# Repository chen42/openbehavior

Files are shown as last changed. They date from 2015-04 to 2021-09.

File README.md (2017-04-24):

# OpenBehavior

This project aims to establish a computing platform for rodent behavior research using the Raspberry Pi computer. We are building devices for conducting operant conditioning, as well as some infrared sensor based assays. We also designed an environmental sensor set that records the temperature, humidity, air pressure, ambient light, noise level, etc. 

These projects are in various stages of development. The following are the most mature projects.

## Operant Licking
This project develops a home cage device for operant licking (fixed ratio, various ratio, or progressive ratio schedules). Detailed description of this project is published in a [PeerJ article]( https://peerj.com/articles/2981/) 

## EnvSensors

This device collects four environmental variables and we have several of them running in the lab. This device is also described in our [PeerJ article](https://peerj.com/articles/2981/)

## RFID 

This project develops a standalone RFID reader for the EM4100 implantable glass chips. We use this daily in the lab.

## Extinction

This device is used to run extinction experiments as described  by [Wang et al. (2014)](www.ncbi.nlm.nih.gov/PubMed/25532105) 

## Motion

This project adds a motion sensor to standard operant chambers.

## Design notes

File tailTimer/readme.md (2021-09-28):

# TailTimer: Automating the tail immersion assay 

# Please do not pull from this repo. Tailtimer submodule has been moved to [this](https://github.com/chen42/tailTimer) repo. All updates will be done there.

The tail immersion assay is a widely used method for measuring acute thermal pain in rodents. TailTimer  uses the Raspberry Pi computer to automatically record both tail withdrawal latency and water temperature. The device has a radio frequency identification (RFID) system that can record the ID of animals. The software recognizes several specific RFID keys as user interface commands, which allows TailTimer to be operated via RFID fobs. We also programmed the device to only allow tests to be conducted when the water is within ± 0.25 °C of the target temperature.

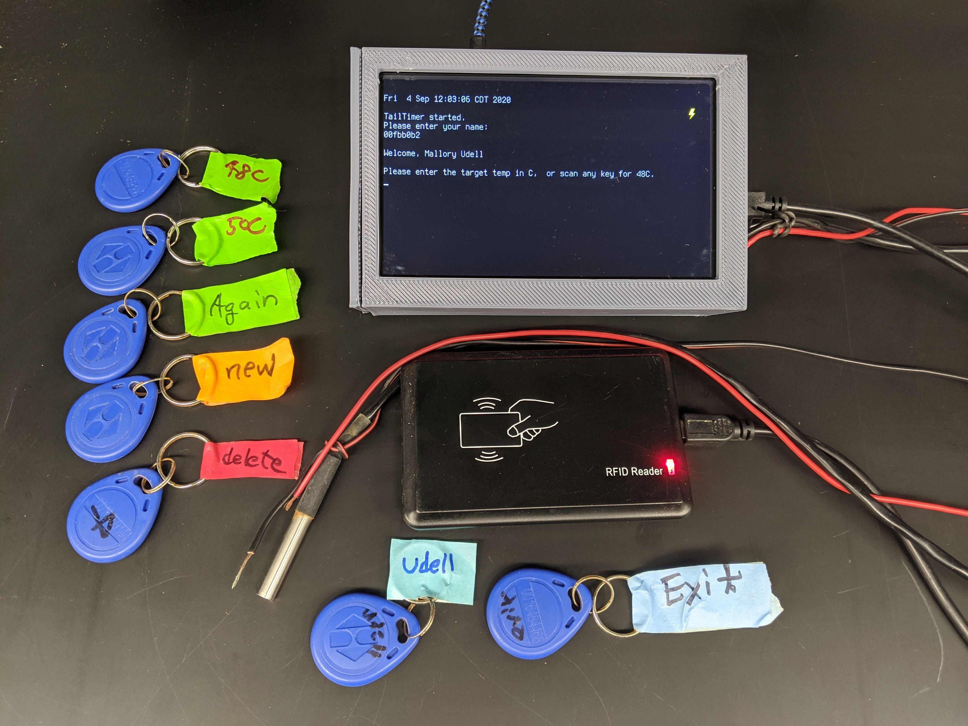
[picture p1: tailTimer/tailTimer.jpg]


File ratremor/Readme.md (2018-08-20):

#Ratremor

Tremor is a common sign of withdrawal from abused drugs. By fixing an ADXL345 accelerometer to the bottom of a platform that is sitting on a set of four balanced springs, we are testing if the z-axis data can be used to measure tremor in rats.

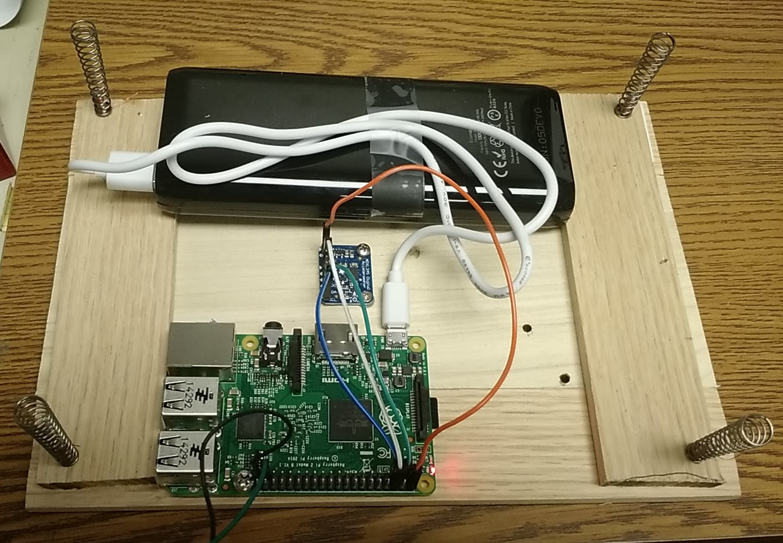
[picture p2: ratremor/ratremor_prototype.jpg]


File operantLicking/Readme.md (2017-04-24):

# Operant Licking

This device uses a RPi to record the licking events on two spouts. It then drives a syring pump to deliver a fixed amount of liquid to the spout, based on the reinforcement schedule in effect (fixed, variable, or progressive ratio).  

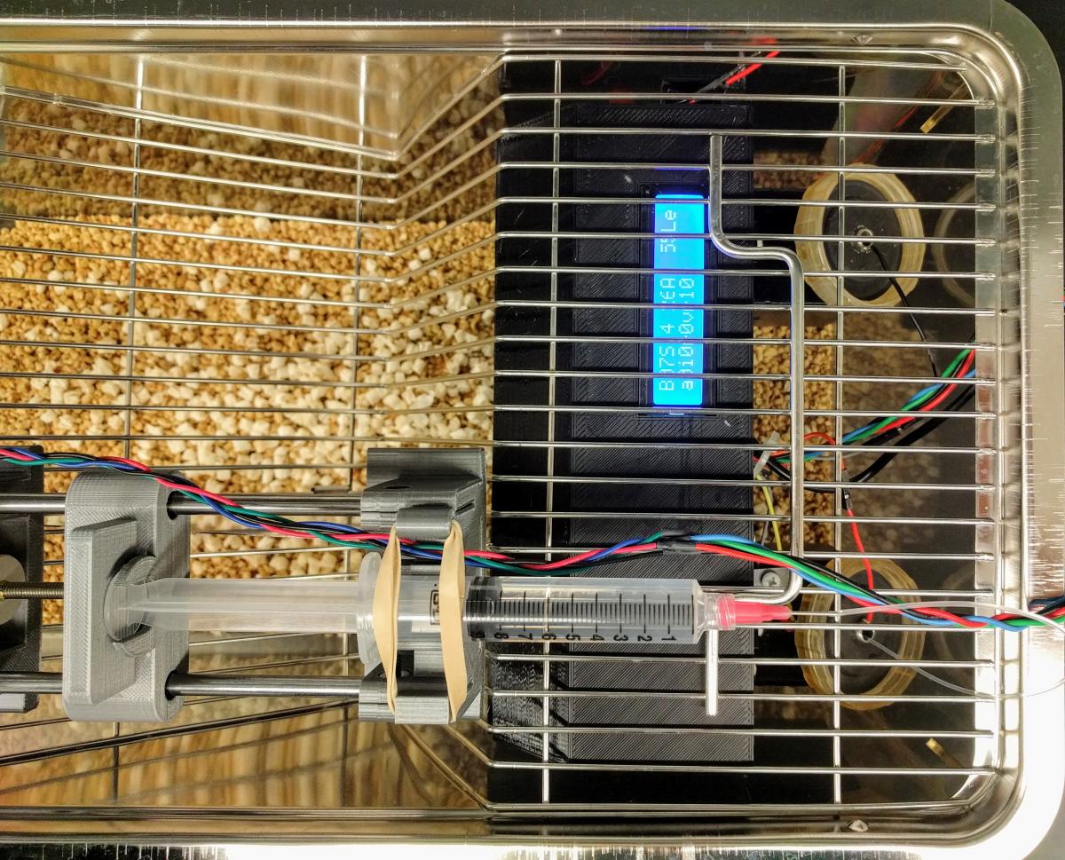
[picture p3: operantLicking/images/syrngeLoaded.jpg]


## [Parts list](PartsList.md) 

## [Assembly instruction](Assembly.md)

Detailed description is published in this [PeerJ Article](https://peerj.com/articles/2981/)

A video of rat licking for sucrose under a VR10 schedule is available [here](https://youtu.be/l3SEo6oAtPM)

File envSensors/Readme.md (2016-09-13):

# Using the Raspberry Pi single board computer to monitor the lab environment

The sensor we use include the HTU21DF for humidity,  TSL2561 for light,  and BMP180 for barometric pressure. Both the HTU21DF and BMP180 have a temperature sensor. So we take the average readout of the two. These sensors are all connected to the Raspberry Pi via I2C.  We also use a I2C  real-time clock (DS1307 from either Adafruit or JBtek. JBtek is cheaper but some of the units we got were not reliable) to ensure the accuracy of the time.  

The location of the device is identified in a file named deviceid located at /home/pi/. The ID stored in this file is used to name the data file. This ID is also entered in the data file. This allows the same program to be deployed at multiple locations. The python logger program is run once every 10 min via cron.

We use this device to monitor the environment of animal housing rooms where the light cycle is reversed. The logger program  writes the lux level during the night to a file called lux.csv. The checklux.py program, also ran via a cron job, checks the lux level during the day and flashes an LED to alert the technician if lights are off during the night.    

## Parts list

Raspberry Pi 2B or 3  [Element 14] (https://www.element14.com/community/community/raspberry-pi)

TSL2561 Lux Sensor [Adafruit] (https://www.adafruit.com/products/439)

BMP180 Pressure Sensor [Adafruit] (https://www.adafruit.com/products/1603)

HTU21D-F Humidity Sensor [Adafruit] (https://www.adafruit.com/products/1899)

SB4 Snappable PC BreadBoard [Amazon] (https://www.amazon.com/gp/product/B00PX52C7Q)

1P-1P female to Female Jump Wire [Amazon] (https://www.amazon.com/gp/product/B00R96X8JS)

Edimax USB WiFi module, not needed if use RPi 3B [Amazon] (https://www.amazon.com/Edimax-EW-7811Un-150Mbps-Raspberry-Supports/dp/B003MTTJOY/)

## Assembly 

### Add wires to the sensors

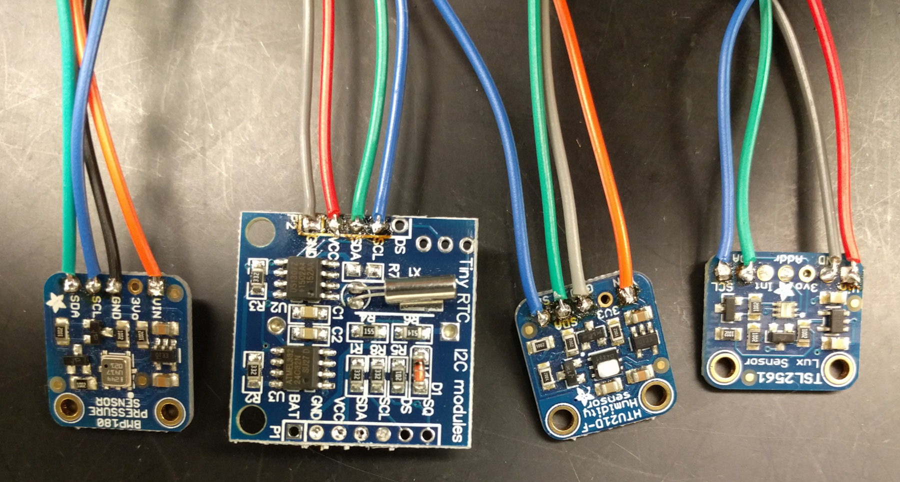
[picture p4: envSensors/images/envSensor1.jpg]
Cut the jumper wire in half. Solder four wires to each sensor (and RTC). We use black (or grey) for ground, red (or orange) for 5V, blue for SCL, and green for SDA. 

### Prepare the breadboard
Drill four holes at the corners. Solder four rows of pin heads (five pins each) to the snappable breadboard. 
We use the two side rows for the GND and 5V. Use the middle two rows for SDA and SCL. 
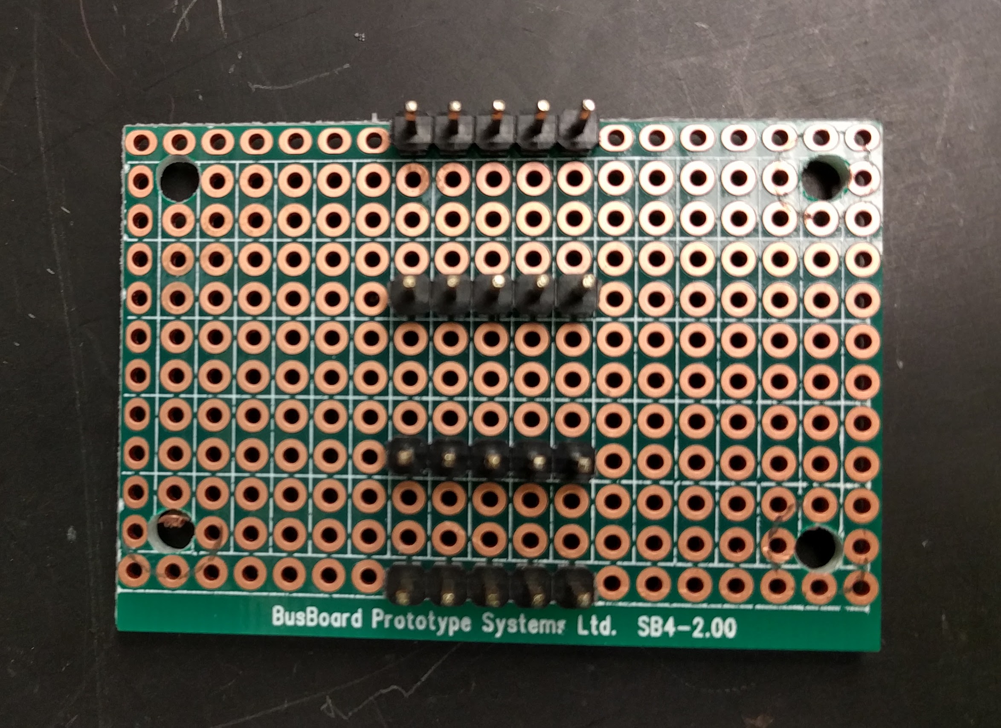
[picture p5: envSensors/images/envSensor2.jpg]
.

Make sure pins on the same head are all connected at the back. (You can solder a short segment of wire to two middle pin heads to connect them).  
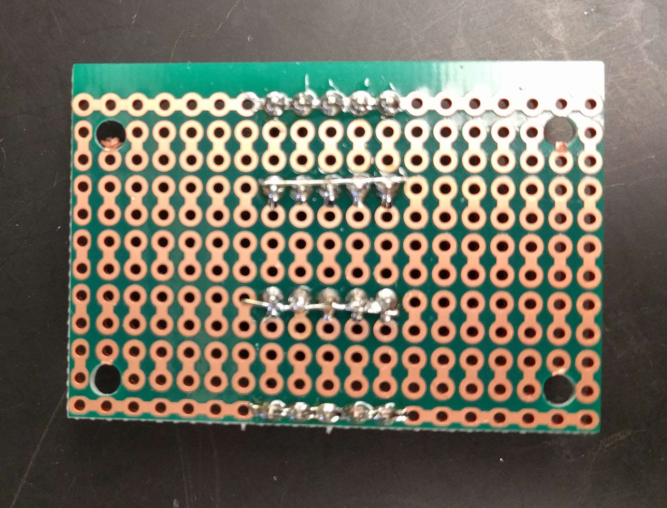
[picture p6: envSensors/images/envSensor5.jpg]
.

### Connect the wires

Connect the sensors and the real-time clock to the pins.
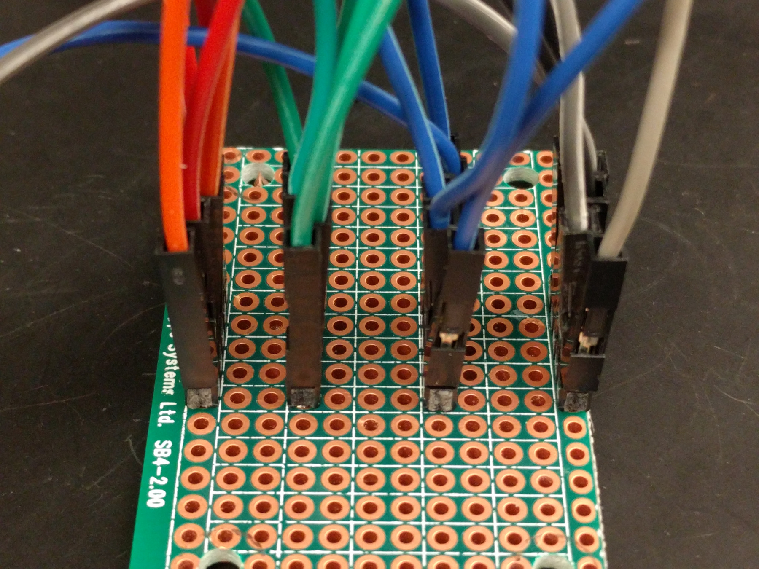
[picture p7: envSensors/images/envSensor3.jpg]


Use one additional sets of four wires to connect the last set of pins to the GND, 5V, SCL, and SDA pins on the RPi.

### Final step

Screw the parts to the 3D printed base.
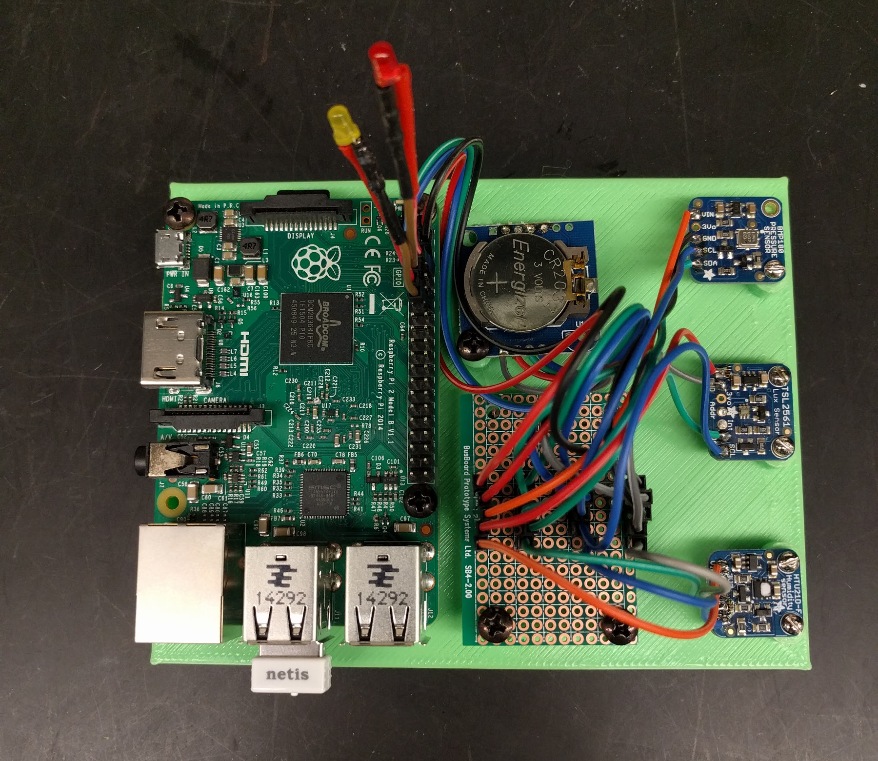
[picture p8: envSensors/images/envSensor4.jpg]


## Software

Clone the repository
```
cd /home/pi/
git clone https://github.com/chen42/openbehavior.git
```

Enable the realtime clock by following these [instructions](https://learn.adafruit.com/adding-a-real-time-clock-to-raspberry-pi/overview)

Edit the /etc/rc.local file to include the following lines  (needed by the RTC and HTU21D-F sensor library)

```
echo ds1307 0x68 > /sys/class/i2c-adapter/i2c-1/new_device
pigpiod &
```

Run the following command to edit cron 

```
sudo crontab -e
```

Add the following line will run the EnvSensor script once every 20 min.

``` 
*/20 * * * python /home/pi/openbehavior/envSensors/env_logger.cron.py 
```

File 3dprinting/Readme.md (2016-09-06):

Design files for 3D printing 
==============================

The frames or cases used for the various devices are located in the devices folder. Here are some misc. objects that we use in the lab. Older files were designed using using <a href="http://freecadweb.org/">FreeCAD</a>. Newer files were designed uing <a href="http://www.openscad.org">Openscad</a>.  You can click on the .stl file and view a 3D rendering of the design using Github's built-in viewer.

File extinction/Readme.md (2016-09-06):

# Using a Raspberry Pi to run extinction sessions

We have several old operant chamber where the electronics are starting to fail. This project uses a RPi to record the number of licks on two spouts. There is also a constantly flashing visual cue during the session. We now use these to run the contextual extinction sessions as described in our earlier papers <a href=https://www.ncbi.nlm.nih.gov/PubMed/25532105> by Wang et al. (2014)  </a> and  <a href="https://www.ncbi.nlm.nih.gov/PubMed/25566005"> by Wang et al. (2014) </a>. ￼ 

The *extinctionCase* holds the RPi.  The *extinctionCueLightPlate* holds the cue light for one side. The *extinctionCueLightBox* is inserted into the *extinctionCase* and holds the other set of cue lights. The *extinctionCaseCover* has an opening for an LCD, which displays session info and data. 

The device is running either from a 5V DC microusb power supply or using a large 5V cell phone backup battery.

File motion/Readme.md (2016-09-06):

#Adding  motion sensors to operant conditioning chambers

## Description
This project adds a motion sensor to the commercial MedPC operant chambers. The motion sensor is controlled by a RPi. The RPi is powered by the 28V power source available in the operant chamber (via a step down converter). The RPi is turned on and off via MedPC programs. The data are stored in the SD card of the Pi. Each operant chamber use one Pi. All the Pi computers are connected by a WiFi network and data are transferred to a remote server via sftp.

## Parts list

Molex connector for 28V. Mfg P/N: 03-06-2032 [Mouser] ( http://www.mouser.com/ProductDetail/Molex/03-06-2032/?qs=%2fha2pyFadugvI%2fznVBilJA6N4bQxmqBpdBoCzb%2f9bbY%3d)  

Molex pin. Mfg P/N: 02-06-2103 [Mouser] (http://www.mouser.com/ProductDetail/Molex/02-06-2103/?qs=%2fha2pyFaduhC0HER4S2%2flGJ0%2fQN3qzJ5F27g%252bKWL4TY%3d)

Motion sensor. [Amazon] (http://www.amazon.com/gp/product/B00FDPO9B8) 

EdiMax WiFi USB. [Amazon] (http://www.amazon.com/gp/product/B003MTTJOY)

Step-down LM2596 power converter. [eBay] (http://www.ebay.com/itm/161476280982)  

## Notes

Two step down DC-DC converters are used. One is set to 5 V to power the RPi. This is always on. The other one is set to 3.3 V. This is only on when the output port in the MedPC is activated. This then controls the on and off of the motion.py program.

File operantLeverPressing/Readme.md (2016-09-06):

#Operant Lever Pressing 

This is one of the earliest attempts we had. It uses a RPi to monitor two levers (i.e. switches). The output is a dry food pellet deliverying device.

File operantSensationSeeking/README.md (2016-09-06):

# Operant Senstation Seeking

This is a device for operant sensation seeking. This needs improvements in several areas based on the alcohol self-admin device. It will be updated when I have time.

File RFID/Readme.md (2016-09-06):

# Standalone RFID Reader

This is a simple device that connects an RDM 6300 RFID reader board to the RPi. The ID of the glass tags is  shown on the LCD.

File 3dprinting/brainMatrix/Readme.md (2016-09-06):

# Brain slicer

## Assembly
See brainMatrix_assembled.stl.  The other three stl files are for printing.

## Procedure
A fresh rat brain is placed in the cutter. Single edge blades are then lowered into the guide slots of the cutter to cut the brain at 1 mm intervals. The slider is then moved out, allowing the cutter to be lowered into the base. The side bars of the base catch the blades and allow the brain sections to be removed one at a time.

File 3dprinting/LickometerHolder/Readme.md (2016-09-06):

# Water spout holder for operant chambers

The tilted bottom one prevents extra liquid causing short circuits. The tall one allows rats with head stages to access the spout. These fits in the standard operant chambers for rats.

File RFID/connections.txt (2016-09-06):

RDM 6300 connections
-------------------
The antenna can be connected in either direction
connect the Tx on the RPi (i.e. pin 8)  to Rx on the board (i.e. PIN 2) 
connect the Rx on the RPi (i.e. pin 10) to Tx on the board (i.e. PIN 1)  
connect the ground on the RPi (i.e. pin 6) to the ground on the board (i.e. Pin 4)
connect the 5V on the RPi (i.e. pin 2) to the power in on the board (i.e. Pin 5)

LCD connections
--------------
RS -> Pin 03 / GPIO 02
EN -> Pin 05 / GPIO 03
D7 -> Pin 07 / GPIO 04
D6 -> Pin 11 / GPIO 17
D5 -> Pin 13 / GPIO 27
D4 -> Pin 15 / GPIO 22

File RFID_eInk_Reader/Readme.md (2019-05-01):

# This is a RFID reader with an eInk hat display

## 2.7 inch e-paper hat
* From [WaveShare.com](https://www.waveshare.com/2.7inch-e-Paper-HAT.htm)
* User manual in [PDF](https://www.waveshare.com/w/upload/3/31/2.7inch_e-paper_hat_user_manual_en.pdf)

## RFID USB reader 
* https://www.amazon.com/Reader-LANMU-125khz-Contactless-Proximity/dp/B07B7H6CQ2

## Software
* Library https://github.com/waveshare/e-Paper/tree/master/2.7inch_e-paper_code/RaspberryPi/
* Steps not described in the user manual
	* enable SPI interface in the PI ```sudo raspi-config```
* For the python demo code from waveshare, make sure the font is present in your system. 
* To run the python code automatically after boot, do the following
  * change the boot into command line and enable auto login with user pi by running ```sudo raspi-config```  
  * add the python program to the end of the .bashrc file for user pi

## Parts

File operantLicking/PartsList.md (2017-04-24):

# Parts list  

Qty 1 for most parts, unless otherwise stated.

Most parts can be purchased from Amazon or Ebay by searching the model number.  

## Operant Licking Device 

Raspberry Pi Model 2B or newer [Element 14](https://www.element14.com/community/community/raspberry-pi).

Edimax WiFi USB connector Model:  EW-7811Un N150 USB 2.0 (not needed for Raspberry Pi 3 or newer).

DS1307 realtime clock with dual I2C connections (Model: AT24C32 IIC) 

12V AC-DC converter (2 Amp) [Amazon](https://www.amazon.com/gp/product/B00PJZQDDO/).

DC-DC step down module adjustable to 5V (Model: LM2596s ASIN: B00W94HW8S) 

Touch sensor (Model: MPR121, 12 channel) [Adafruit](https://www.adafruit.com/products/1982).

Motion sensor (Model: HC-SR501)  

RFID reader (Model: RDM 6300) [Amazon](https://www.amazon.com/gp/product/B00KBN01VY/).

RFID glass tags and injection syringe (EM4100 encoding) [AliExpress](https://www.aliexpress.com/item/RFID-glass-4x20-application-logistics-patrol-asset-identification-management-security-frequency-125KHZ/931328784.html).

LCD 16 x 2 characters (Model HD44780)  

10K ohm potentiometer (if the LCD does not come with one) [Amazon](https://www.amazon.com/gp/product/B00OK9DEL4).

5 mm LED (white, for cue light).

3 mm LED (Assorted colors, for signals).

100 om resister Qty: 3.

Omal (TM) 2 x 40 pcs 20 cm 1P-1P female to female bread jump wire (or other brands).

Stainless steel flux, such as  [Amazon](https://www.amazon.com/gp/product/B001HWE9A2) 

Solid core Hook-up Wire 22 AWG  [Sparkfun](https://www.sparkfun.com/products/11367)

### Syringe Pump

LM6UU linear ball bearing bushing  Qty: 2 per pump [Amazon](https://www.amazon.com/gp/product/B00NQ2DPV0).

625Z single shielded deep groove ball bearing  [Amazon](https://www.amazon.com/gp/product/B008ASXTZM/).

NEMA 11 step motor [Pololu](https://www.pololu.com/product/1205). 

Elegoo Step motor controller with heat sink (Model: A4988) [Amazon](https://www.amazon.com/gp/product/B01GJJGRF2).

18-8 Stainless stell threaded Rod M5-0.8 thread [Amazon](https://www.amazon.com/gp/product/B00G3R7J1W/).

CND motor shaft coupler 5mm to 5mm [Amazon](https://www.amazon.com/gp/product/B00DCAISM2).

Steel Rod 6mm Diameter [Amazon](https://www.amazon.com/gp/product/B0050RMVLE).

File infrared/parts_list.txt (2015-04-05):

items from sparkfun.

Infrared Emitter & Detector Set:
SEN-00241

Emitter:
LTE-302

Detector:
LTR-301

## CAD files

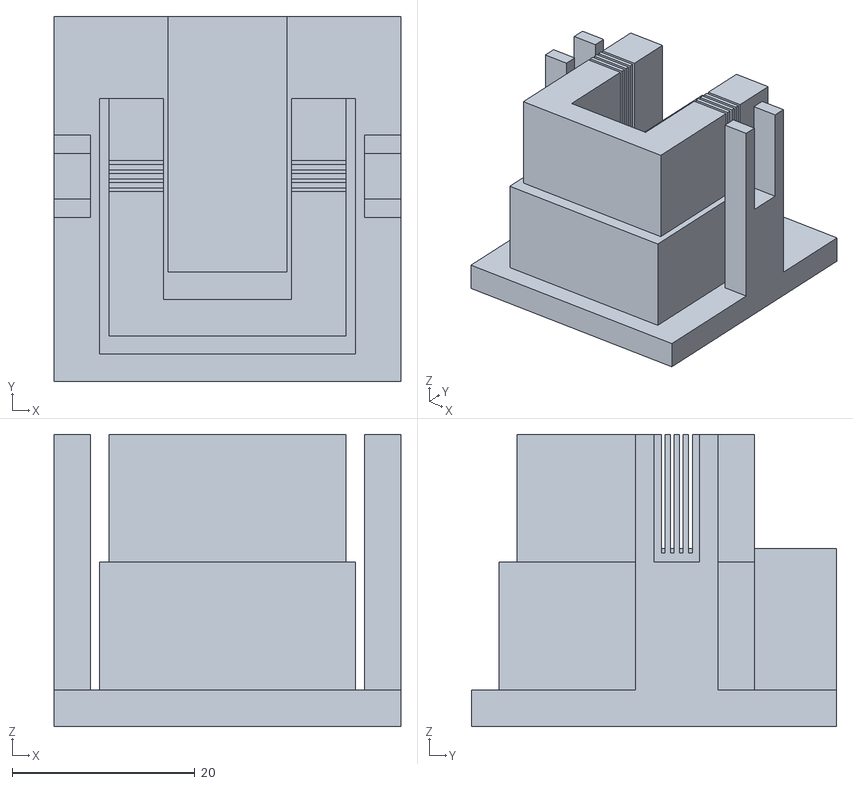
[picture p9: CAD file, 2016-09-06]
3dprinting/brainMatrix/brainMatrix_assembled.stl
38.0 x 40.0 x 32.0

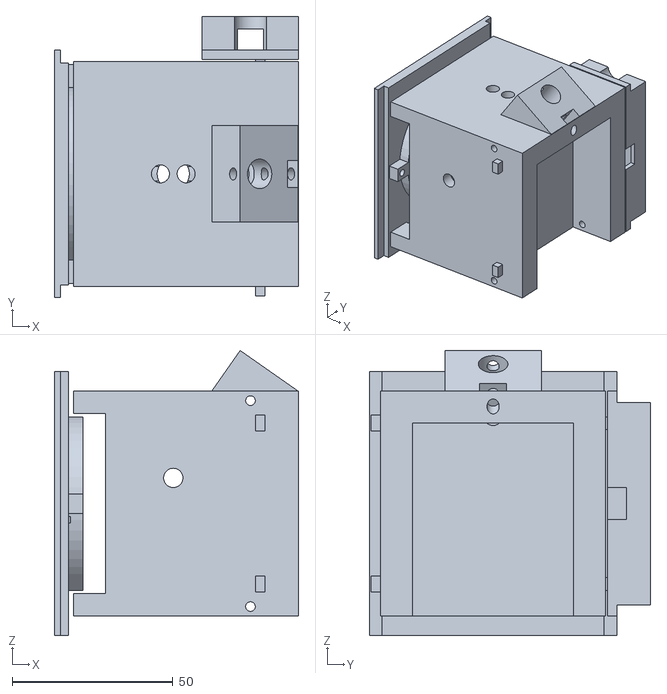
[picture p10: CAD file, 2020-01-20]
socialDrinking/openscad/rfid_waterspout_complete.stl
76.0 x 87.5 x 88.6

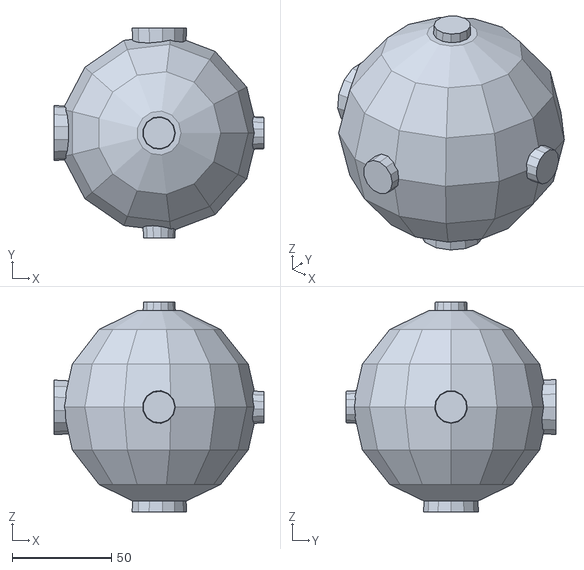
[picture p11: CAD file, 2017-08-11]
3dprinting/ball/ball_lo_res.stl
106.0 x 106.0 x 106.0

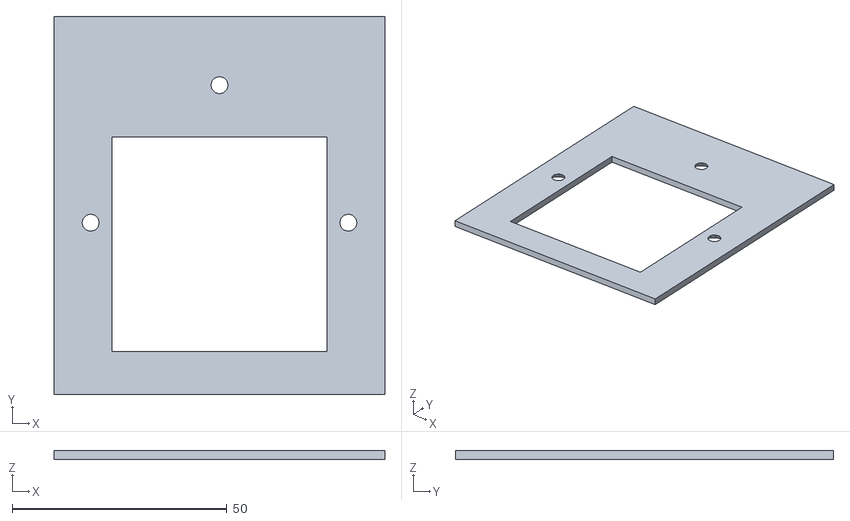
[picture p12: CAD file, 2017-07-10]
3dprinting/LickometerHolder/operant_chamber_spout_holder_plate.stl
77.0 x 88.0 x 2.00

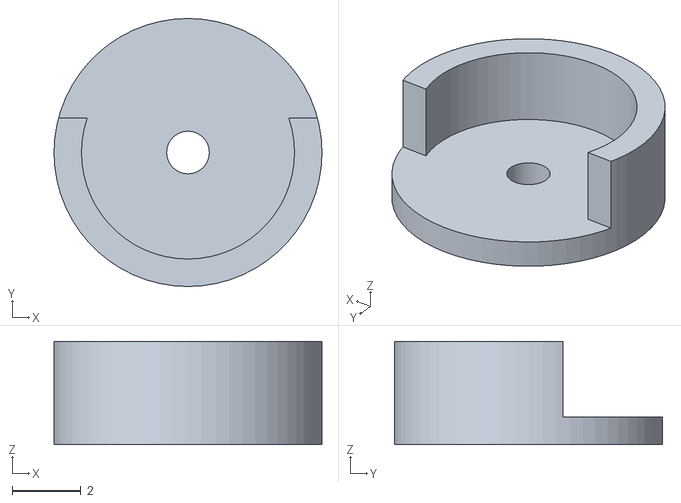
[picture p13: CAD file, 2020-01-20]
3dprinting/mouse_eartag/mouse_eartag.stl
7.80 x 7.80 x 3.00

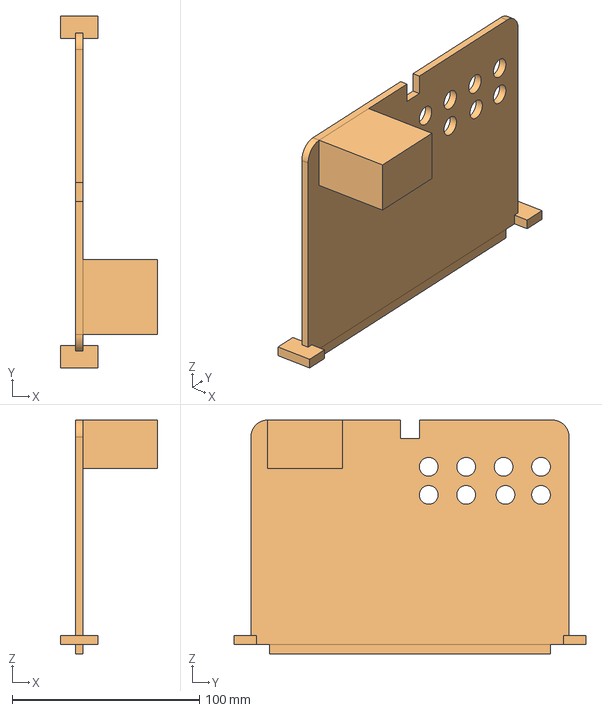
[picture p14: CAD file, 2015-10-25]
3dprinting/mouseBoxDivider/MoueBoxInsertPart1.fcstd
52.0 x 188.0 x 125.0 mm
topextension

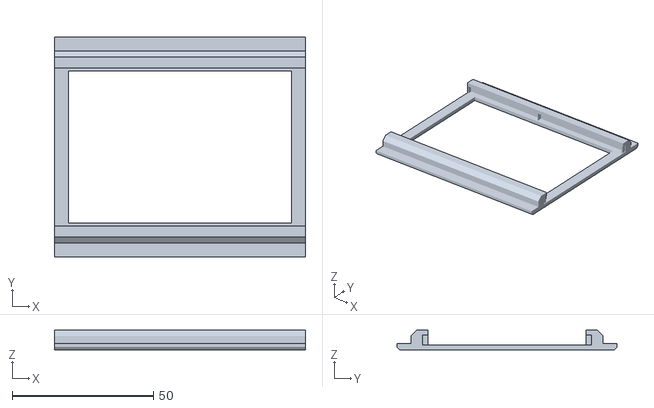
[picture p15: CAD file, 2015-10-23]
3dprinting/mouseNosePokeInRatBox/mouseNosePokeForRat.stl
89.0 x 78.0 x 7.00

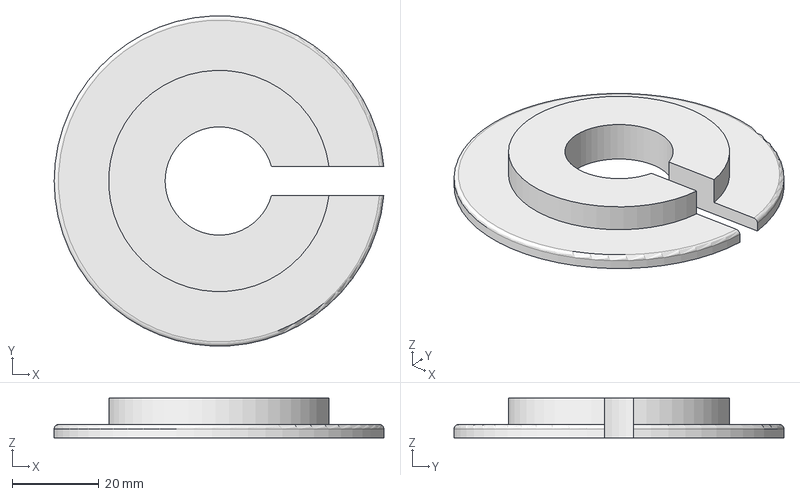
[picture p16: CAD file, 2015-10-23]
3dprinting/operantChamberTopCover/rat.operant.chamber.center.cover.fcstd
76.1 x 76.2 x 9.20 mm

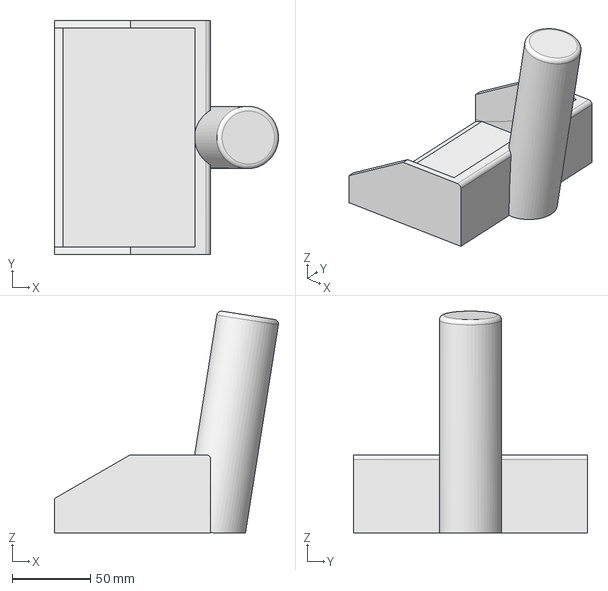
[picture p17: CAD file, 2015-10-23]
3dprinting/poopScoop/RatPoopScoop.fcstd
143.4 x 150.0 x 142.0 mm

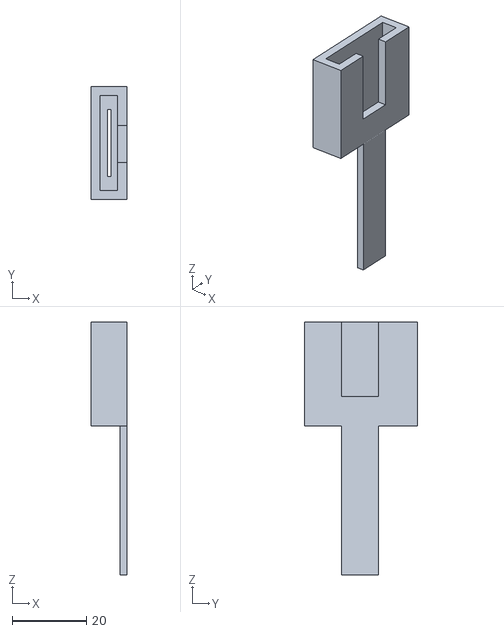
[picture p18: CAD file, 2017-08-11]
3dprinting/raspberrypi_camer_case/rpi_camera_mount.stl
9.80 x 30.5 x 68.0

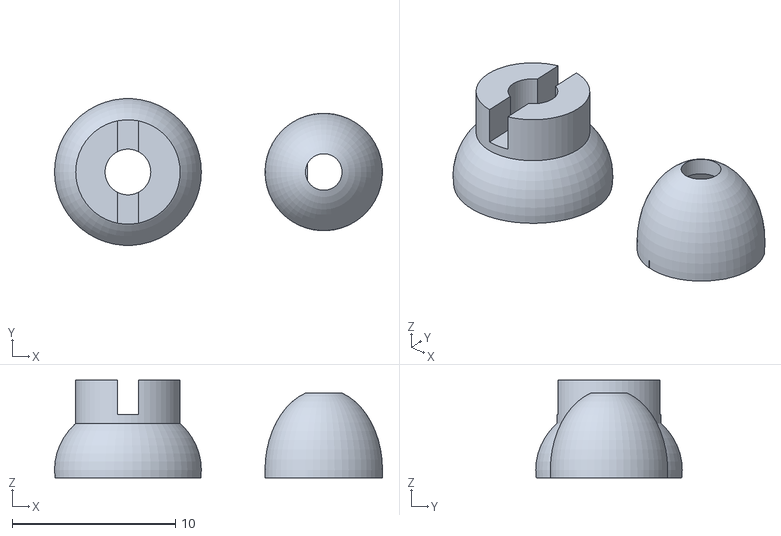
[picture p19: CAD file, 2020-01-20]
3dprinting/rat_eartag/rat_eartag.stl
20.1 x 8.98 x 6.00

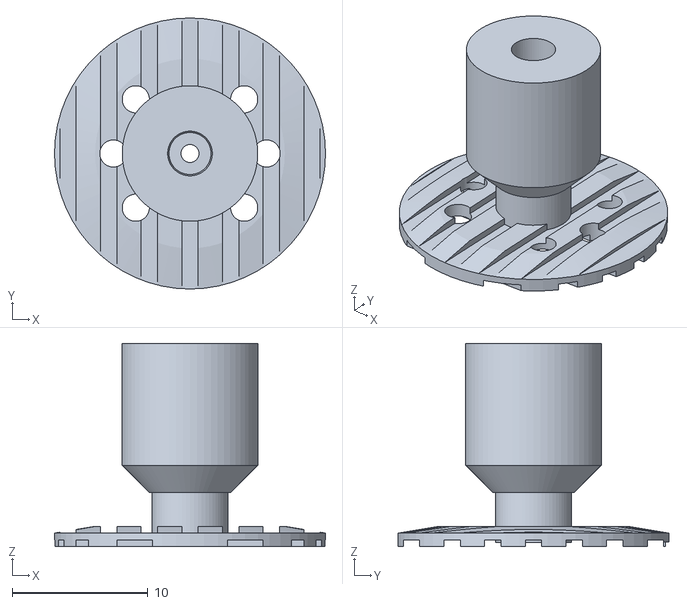
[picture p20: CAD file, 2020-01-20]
3dprinting/ratButton/ratButton.stl
20.0 x 20.0 x 15.0

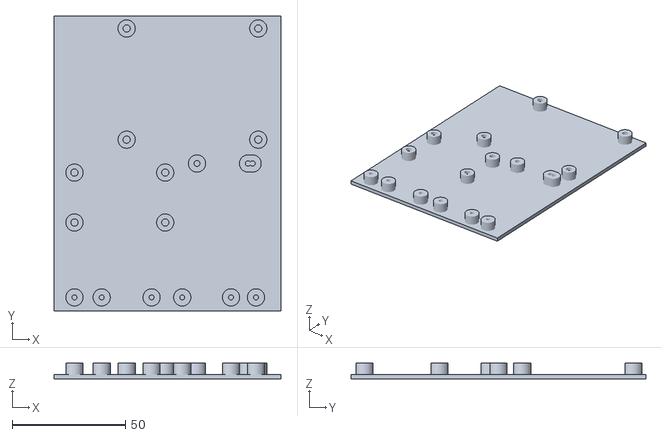
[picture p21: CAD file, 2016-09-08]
envSensors/3D_design_frame/envSensorBoard.stl
100.0 x 130.0 x 7.00

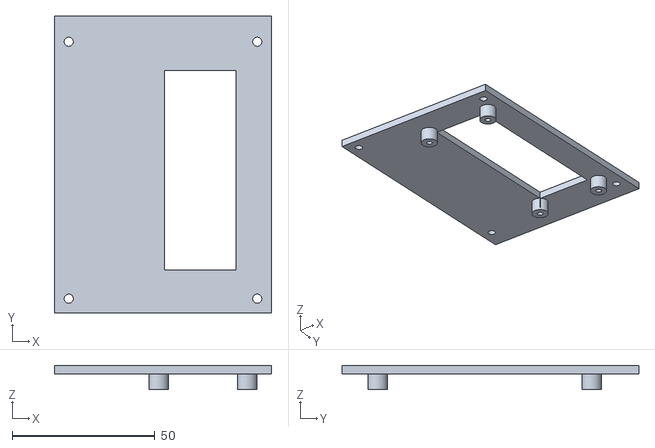
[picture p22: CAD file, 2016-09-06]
extinction/extinctionCaseCover.stl
76.0 x 104.0 x 8.50

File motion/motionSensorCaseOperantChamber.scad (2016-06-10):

$fn=100;

module mounting_m25(innR=1.6, h=10){ // screw 
	difference(){
		color("orange") cylinder(r=3.8, h);
		cylinder(r=innR, h=10);
	}
}

module mounting_pi(){
	translate([-58/2,-49/2,0]) mounting_m25();
	translate([58/2,-49/2,0]) mounting_m25();
	translate([-58/2,49/2,0]) mounting_m25();
	translate([58/2,49/2,0]) mounting_m25();
	translate([-10,0,0]) cube([85,56,0.1], center=true);
} 

module volhouse () {  /* voltage converter*/
	difference(){
		cube([22,27,12],center=true);
		cube([18,23,12.1],center=true);
	}
}
module mounting(){
	cube([14,12,3],center=true);
}

module col2nd(){
	difference(){
		cube([6,6,12], center=true);
		screw();
	} 
}
module cover(){
	difference() {
		cube([x0,y0,3], center=true);
		rotate([0,0,180]) translate([0,0,-20]) color("blue") screw4();
	}
	y=-20;
	x=16;
	z=4.5;
	translate([x,y,z]) volhouse();
	translate([-x,y,z]) volhouse();
	translate([x+13,y, z]) col2nd();
	translate([-x-13,y, z]) col2nd();
}


module col(){
		cube([8,8,12],center=true);
}
module col4(){
	zz=15;
	translate([x0/2-4, y0/2-9, zz]) col();
	translate([-x0/2+5, y0/2-9, zz]) col();
	translate([x0/2-5, -y0/2+5, zz]) col();
	translate([-x0/2+5, -y0/2+5, zz]) col();

}

module screw() {
	translate([0,0,-10])	cylinder(r=1.6, h=20);
}


module screw4(){
	zz=15;
	translate([x0/2-5, y0/2-9, zz]) screw();
	translate([-x0/2+5, y0/2-9, zz]) screw();
	translate([x0/2-5, -y0/2+5, zz]) screw();
	translate([-x0/2+5, -y0/2+5, zz]) screw();
}

x0=76;
y0=104;
z0=42;


module case(){
	difference(){
		cube([x0, y0, z0], center=true); // outside 
		translate([0,0,4]) cube([x0-4, y0-4, z0+5], center=true); // inside 
		translate([0,y0/2,1]) cube([56, 8, 41], center=true);
		translate([0,-40,21]) rotate([90,0,0]) cylinder(r=3,h=30); // power cords
		translate([-4,-53,-z0/2+10]) cube([20,10, 5], center=true); // sdcard slot  
	}
	translate([-4,-17,-z0/2+1]) rotate([0, 0, -90]) mounting_pi();
	difference(){
		col4();
		screw4();
	}
}

module volcover(){
	sx=29;
	sy=-20;
	sz=10;
	difference(){
		translate([0, sy,sz]) cube([64,8,2],center=true);
		translate([sx, sy,sz])screw();
		translate([-sx, sy,sz])screw();
	}
}

module motionBoxPos() {
	translate([0,-2/2,0]) 	cube([63.4, 2,40], center=true) ; //backplate
	translate([0,-2/2-4.5,0]) cube([63.4, 2,40], center=true) ;//bbackplate
	translate([0,-25,0]) cube([77.4, 2,40], center=true); //faceplete
	translate([0,-25/2,0])	cube([55.4,25,40], center=true); // outside 
}

module motionBoxNeg() {
	translate([0,-25/2+2, 0]) cube([51.4, 26, 31], center=true); // inside 
	translate([14.5,0,0]) rotate([90,0,0]) cylinder(r=1, h=25); // motion sensor mounting screw
	translate([-14.5, 0,0]) rotate([90,0,0]) cylinder(r=1, h=25); // motion sensor mounting screw
	rotate([90,0,0]) cylinder(r=4.5, h=30); // motion sensor proper
	translate([0,-25,0])rotate([90,0,0]) cylinder(r1=4.5, r2=14,h=3); // motion sensor proper
}

module motionBoardBox(){
	difference() {
		motionBoxPos();
		motionBoxNeg();
	}
}

//case();
//translate([0,48,1]) rotate([0,0,180] ) motionBoardBox();
//translate([0,0,25]) rotate([0,180,180]) cover();
color("yellow") volcover();

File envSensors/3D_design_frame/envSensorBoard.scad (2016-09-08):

$fn=60;

translate([-4,0,0]) pi();
translate([-65,-100,0]) base();
translate([-60,-65,0]) color("red") devboard();
translate([-2,-35,0]) rtc();
translate([13,-94,0]) humidity();
color("green") translate([-22,-94,0]) lux();
color("cyan") translate([-56,-94,0]) barometer();

module barometer(){
	m25(innR=1.1);
	translate([12,0,0]) m25(innR=1.1);
}	

module humidity(){
	m25(innR=1.1);
	translate([11,0,0]) m25(innR=1.1);
}	

module lux(){
	m25(innR=1.1);
	translate([13.5,0,0]) m25(innR=1.1);
}	


module devboard() {
	translate([4,4,0]) m25();
    translate([44,4,0]) m25();
   	translate([4,26,0]) m25();
   	translate([44,26,0]) m25();
}

module rtc(){
	m25(innR=1.3);
	difference(){
		union(){
			translate([22.5,0,0]) cylinder(r=3.8, h=7);
			translate([24.5,0,0]) cylinder(r=3.8, h=7) ;
		}
		translate([22.5,0,0]) cylinder(r=1.2, h=10);
		translate([24.5,0,0]) cylinder(r=1.2, h=10); 
	}
}


module m25(innR=1.6, h=7){ // screw 
	difference(){
		color("orange") cylinder(r=3.8, h);
		cylinder(r=innR, h=10);
	}
}

module pi(){
	translate([-58/2,-49/2,0]) m25();
	translate([58/2,-49/2,0]) m25();
	translate([-58/2,49/2,0]) m25();
	translate([58/2,49/2,0]) m25();
//	translate([-10,0,0]) cube([85,56,0.1], center=true);
} 

module base(){
	color("grey") cube([100,130,2]);
}

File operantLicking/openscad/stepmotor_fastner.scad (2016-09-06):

$fn=40;
module step_motor_fastener (){
	difference(){
		cube([13, 9, 3],center=true);
		translate([4,0,-3]) cylinder(r=1.7, h=8);
	}
}

step_motor_fastener() ;

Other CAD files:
motion/motionSensorCaseOPCover.stl
operantLicking/openscad/alcoholSelfAdmin_cueLightFastner.stl
operantSensationSeeking/freecad/roof.stl
RFID/rfidReaderTop.stl
extinction/extinctionCase.scad
3dprinting/LickometerHolder/operant_chamber_spout_holder_plate.scad
3dprinting/LickometerHolder/rat.spout.holder.plate.stl
3dprinting/LickometerHolder/rat.water.holder.plate.FCStd
3dprinting/LickometerHolder/rat.water.spout.e-phyis.faceplate.fcstd
3dprinting/LickometerHolder/rat.water.spout.holder.tilted.fcstd
3dprinting/LickometerHolder/ratSpoutHolderPlate.scad
3dprinting/LickometerHolder/water.spout.holder.ephyis.face.plate.stl
3dprinting/LickometerHolder/waterbottleholder.tiltedbottom.stl
3dprinting/ball/ball.scad
3dprinting/ball/ball_hi_res.stl
3dprinting/brainMatrix/brainMatrix.scad
3dprinting/brainMatrix/brainMatrix_base.stl
3dprinting/brainMatrix/brainMatrix_cutter.stl
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

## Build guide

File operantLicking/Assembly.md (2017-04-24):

# Assembling the operant licking device

## 3D printed frame
The frame is printed in two parts and put together using superglue. Because of its size, the results are much better if you print it on a heated platform. You can also print it as a single piece, but you need to enable 'supports' and remove them afterwards. 
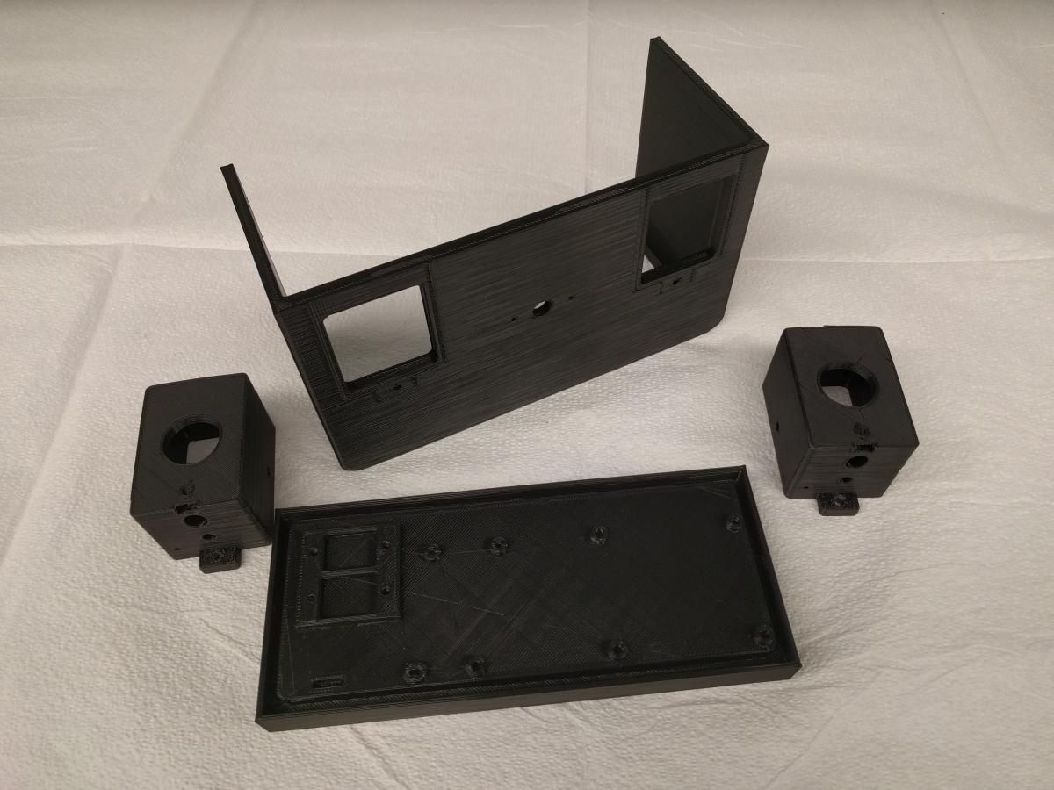
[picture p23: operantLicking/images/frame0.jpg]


Use sand paper to clean a small area of a spout. Then older a segment of solid core hookup wire to a spout with the help of one drop of stainless steel Flux (see parts list).  
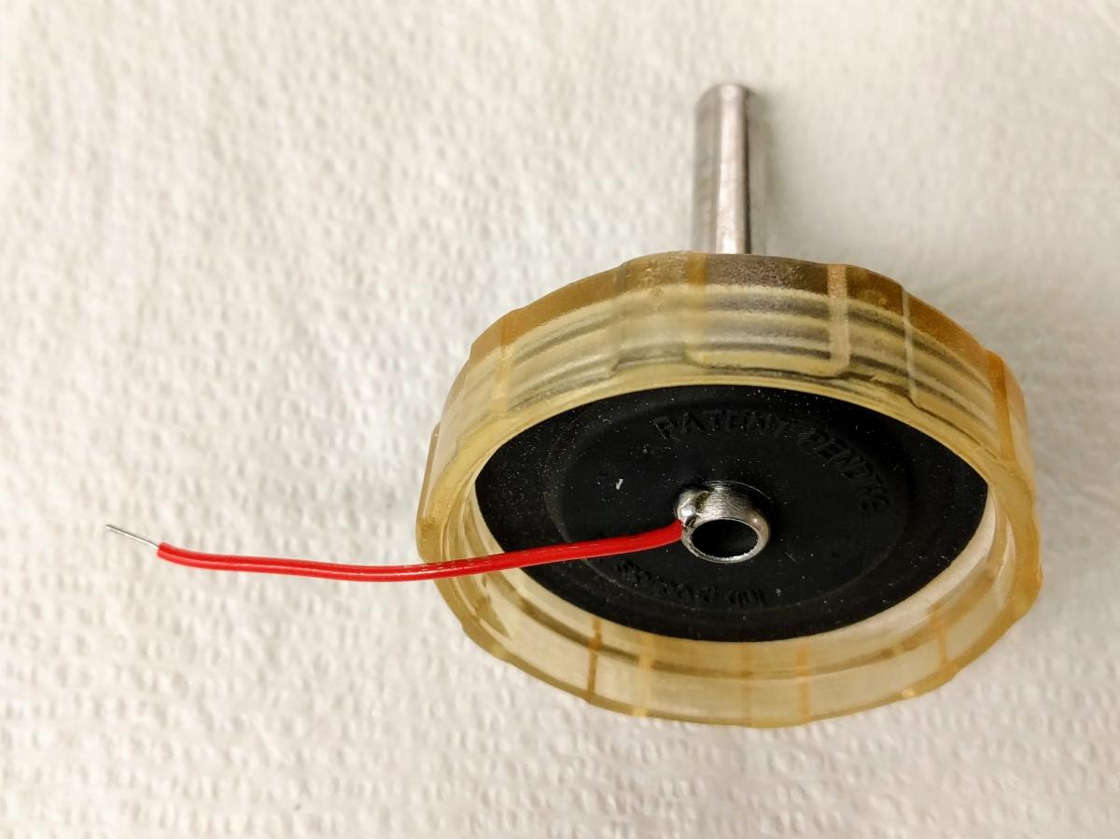
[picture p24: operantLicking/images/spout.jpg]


Solder one 100 ohm resister to a 5 mm LED (clear). Cover it with a short segment of heat shrink tubing.  
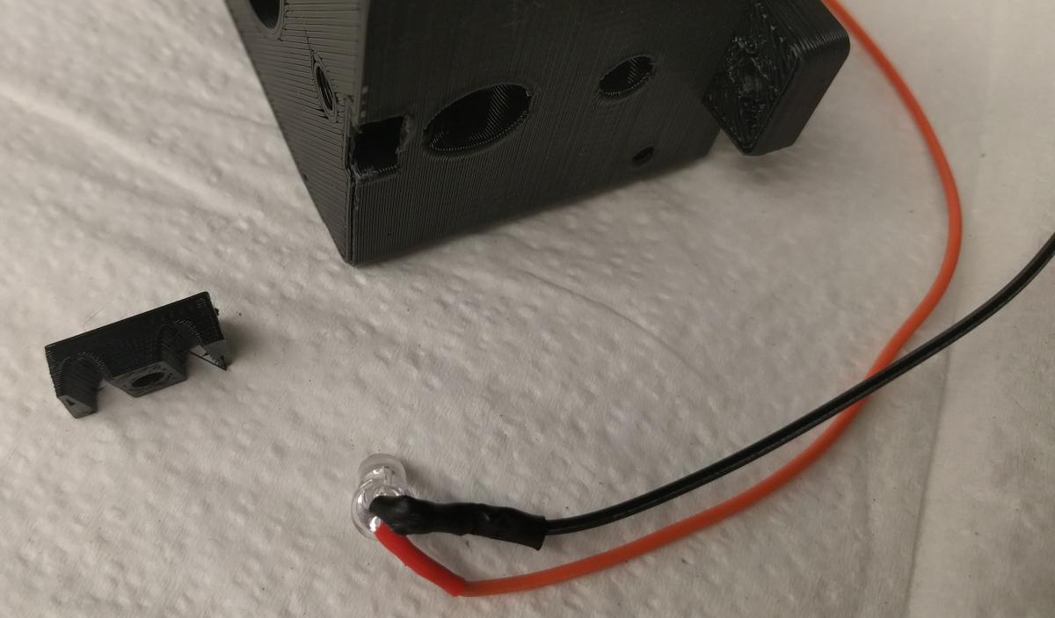
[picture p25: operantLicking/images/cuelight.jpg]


Insert the LED into the cue light slot. Fix it in place using the small piece.  
Add a hex nut to the small opening on the spout holder. Use a thumbscrew to hold the spout (not shown) in place.
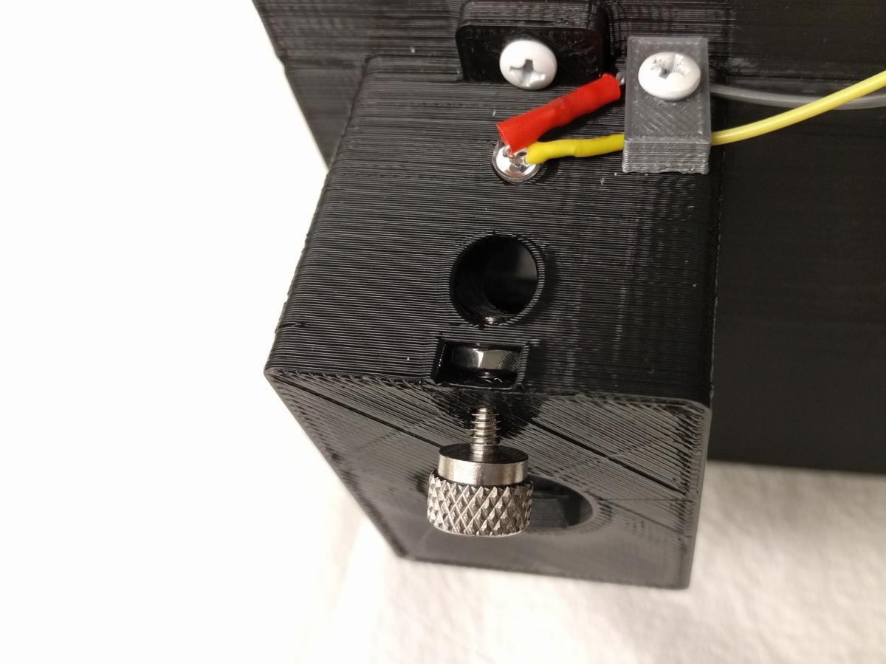
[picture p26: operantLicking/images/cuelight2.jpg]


## Switch Board
The switches are used to provide bidirectional manual control of the syringe. 
The board also has two LEDs. The green LED indicates motion events and the red LED indicates licking events. The resistors are 100 ohm. 
The two holes are used for attaching the board to the top cover of the 3D printed frame.
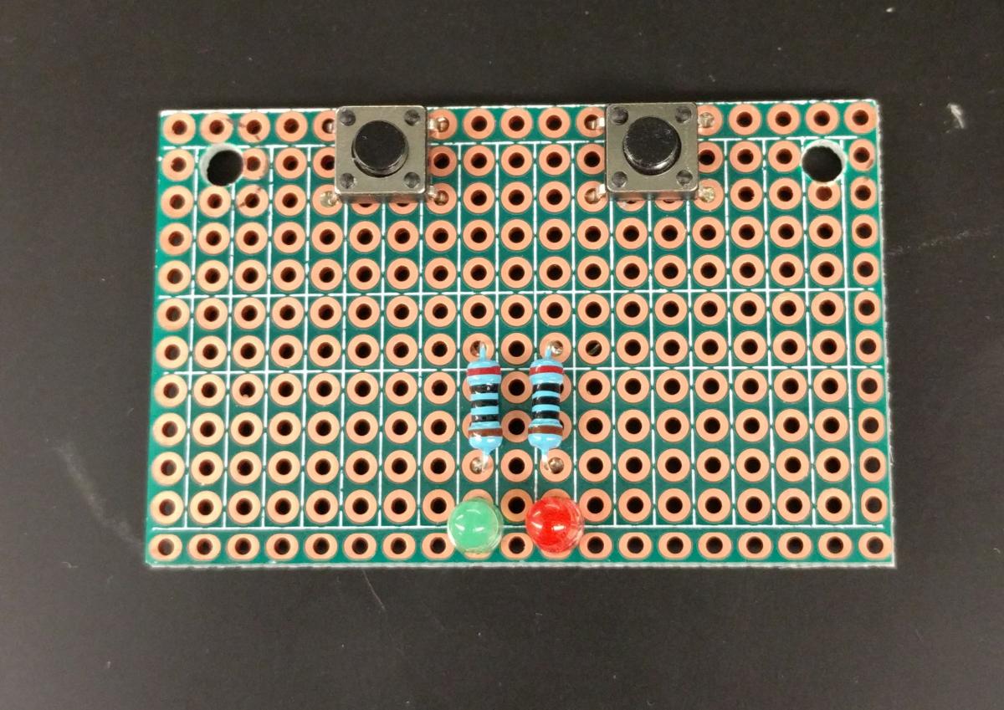
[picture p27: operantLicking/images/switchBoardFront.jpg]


The switch board also provides ground and 5V power to several boards (RFID reader, real time clock, touch sensor).  
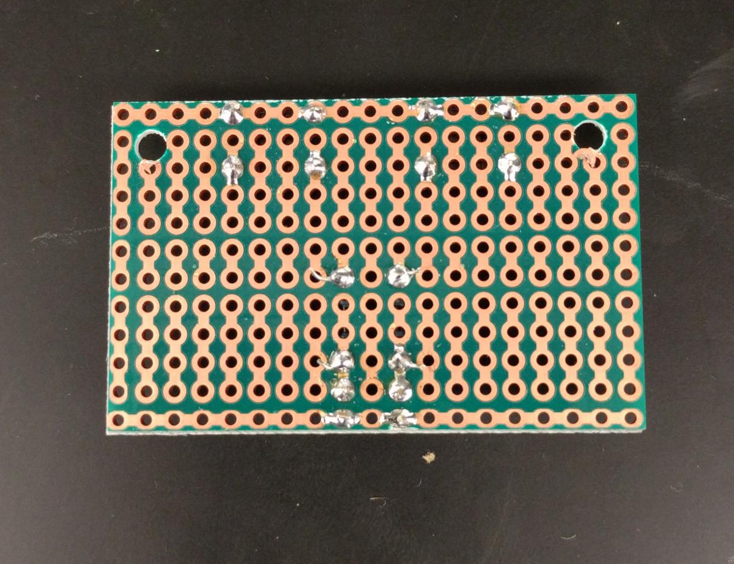
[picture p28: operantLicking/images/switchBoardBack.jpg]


The back side of the switch board with wires added. The blue and white wires are for the two switches. The yellow and green wires are for the LEDs. Solid core hook-up wired were used here but soldered header pins also work, as shown in the assembled model.  
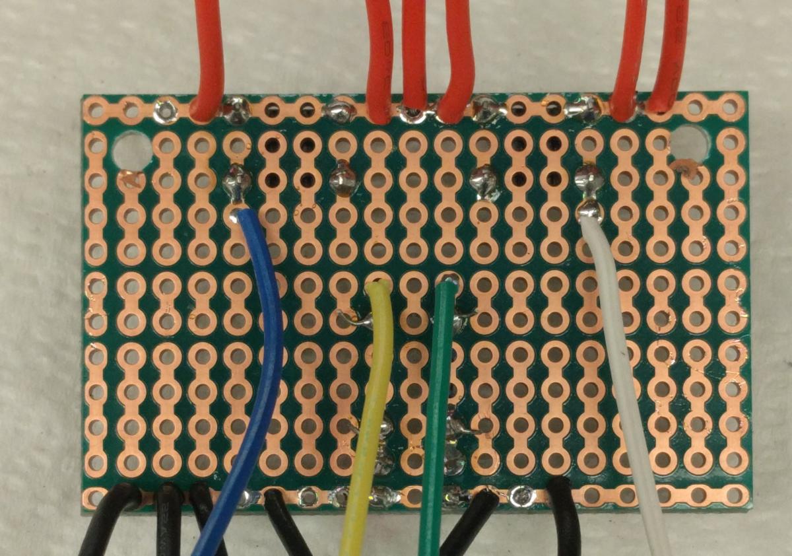
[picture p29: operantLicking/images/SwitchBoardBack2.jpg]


## RFID Reader 

Extend the length of the RFID antenna by soldering two segments of wires (approximately 12 inches) between the antenna loop  and the connector. 

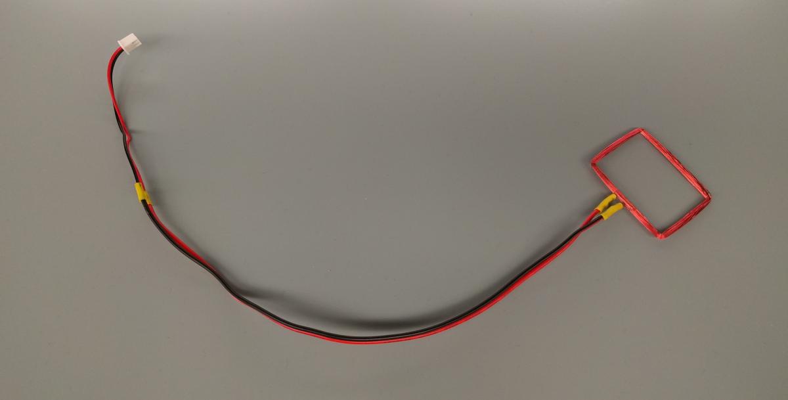
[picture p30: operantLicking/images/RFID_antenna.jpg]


Place the antenna loop next to the 3D printed handle, tape the wire to the handle. Then insert the antenna loop into the 3D printed frame (below). 

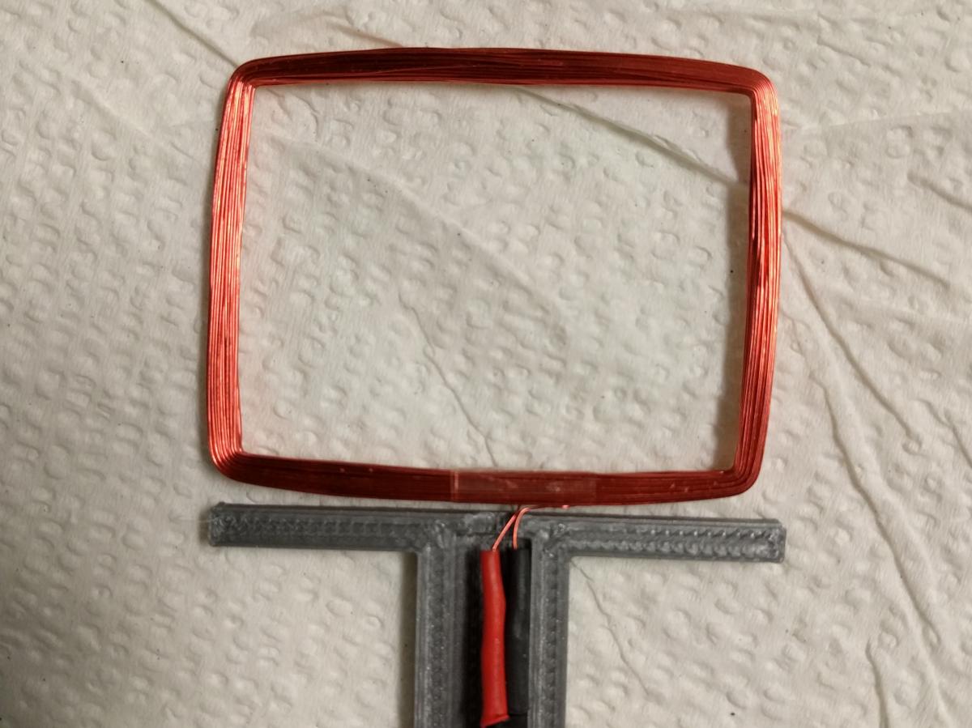
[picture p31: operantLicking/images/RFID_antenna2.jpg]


Tape the handle and the frame together.

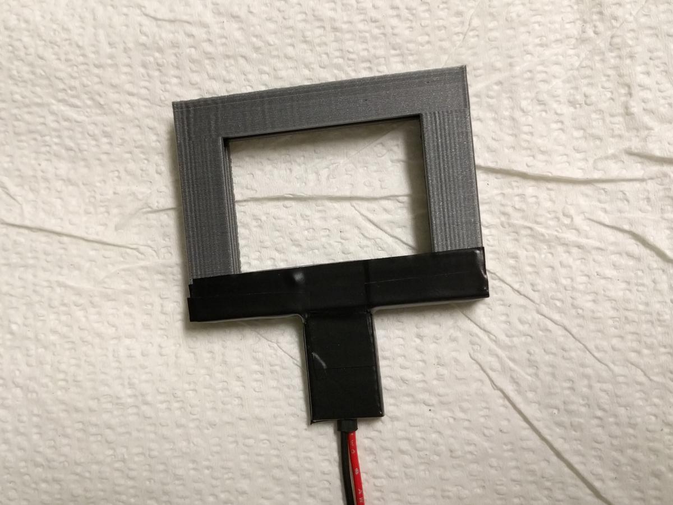
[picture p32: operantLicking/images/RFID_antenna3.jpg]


The RFID board is fixed on top of the frame by using connection pins. Insert pin headers into the openings in the frame. Glue it.

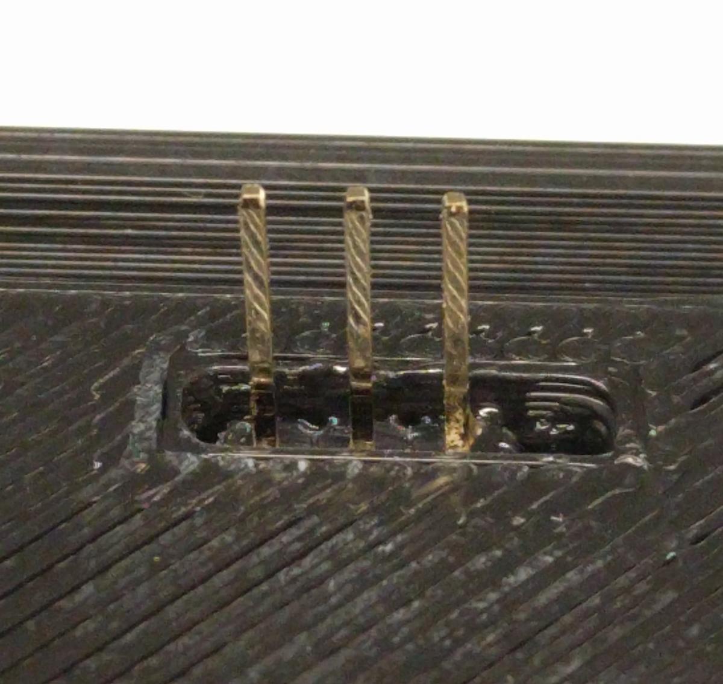
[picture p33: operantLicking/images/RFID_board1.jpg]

Insert the RFID board.

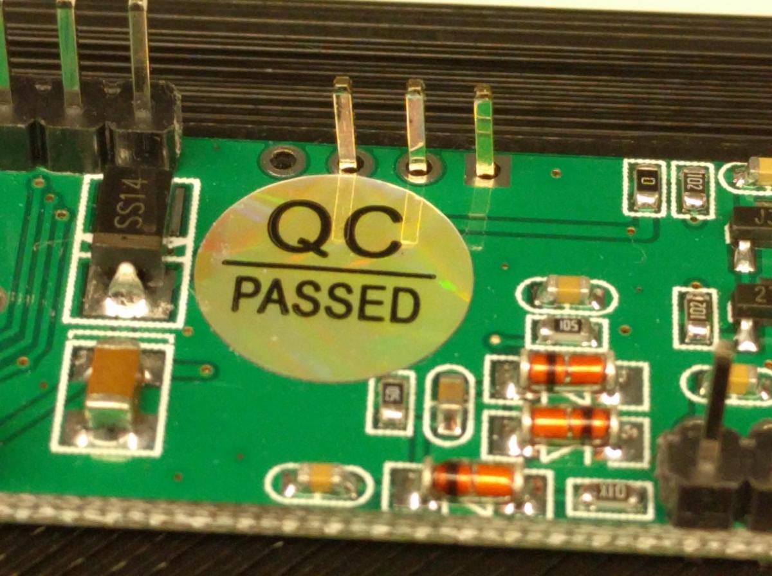
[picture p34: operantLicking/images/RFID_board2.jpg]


Push three pins out of the header and use the remaining to fasten the RFID board in place. Connect the RFID antenna.
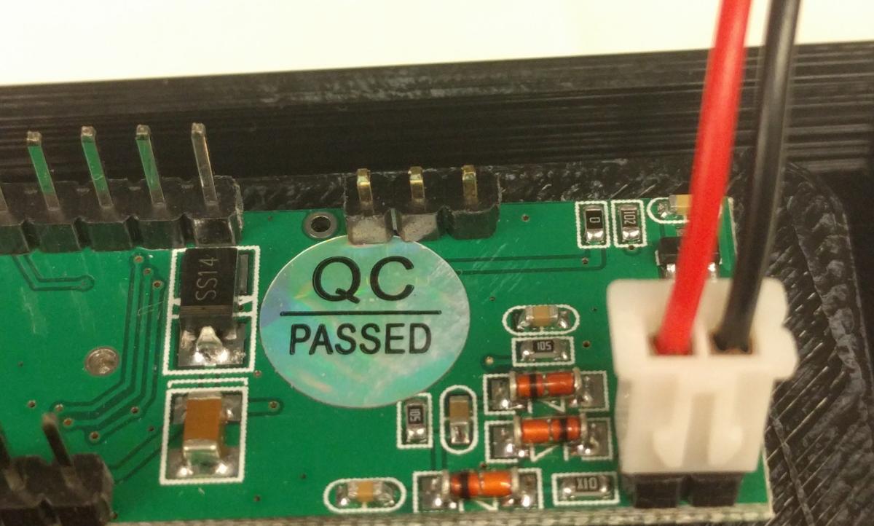
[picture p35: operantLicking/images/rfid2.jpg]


# Motion Sensor
Bend the three pins on the motion sensor one by one to 90 degrees. Use two screws to hold the sensor on the frame.
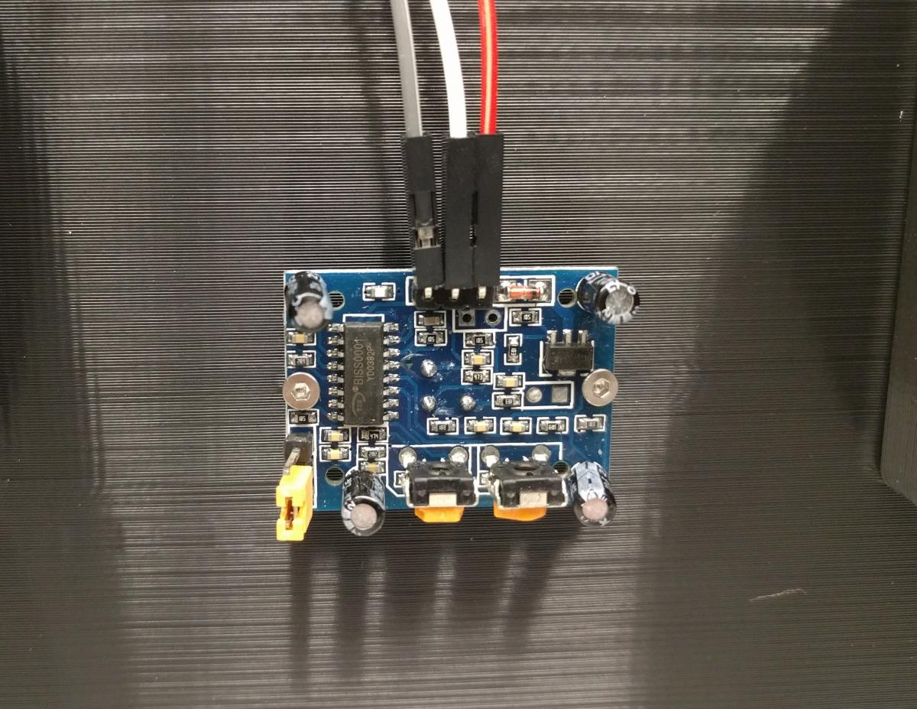
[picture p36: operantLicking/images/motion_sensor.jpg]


## LCD
The LCD needs a 10 K ohm potentiometer. Bend the wires as shown. 
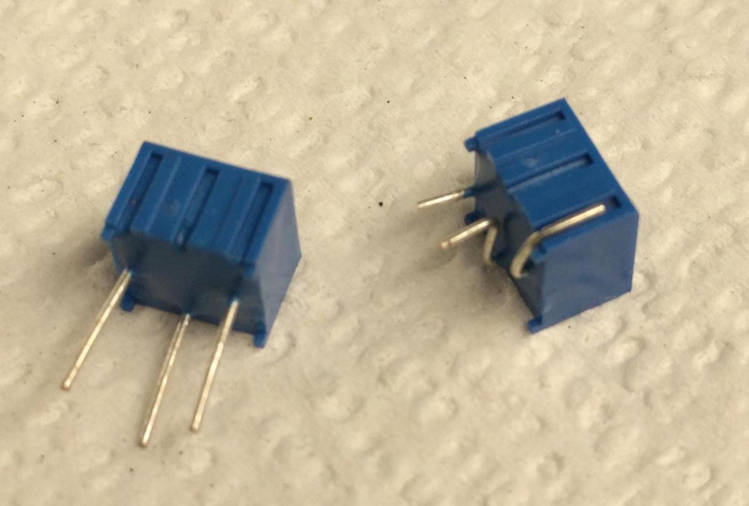
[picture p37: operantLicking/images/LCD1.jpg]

Solder it to the LDC. The middle wire of the potentiometer is connected to the 3rd pin of the LCD.  The other two wires are connected to pins 1 and 2. 
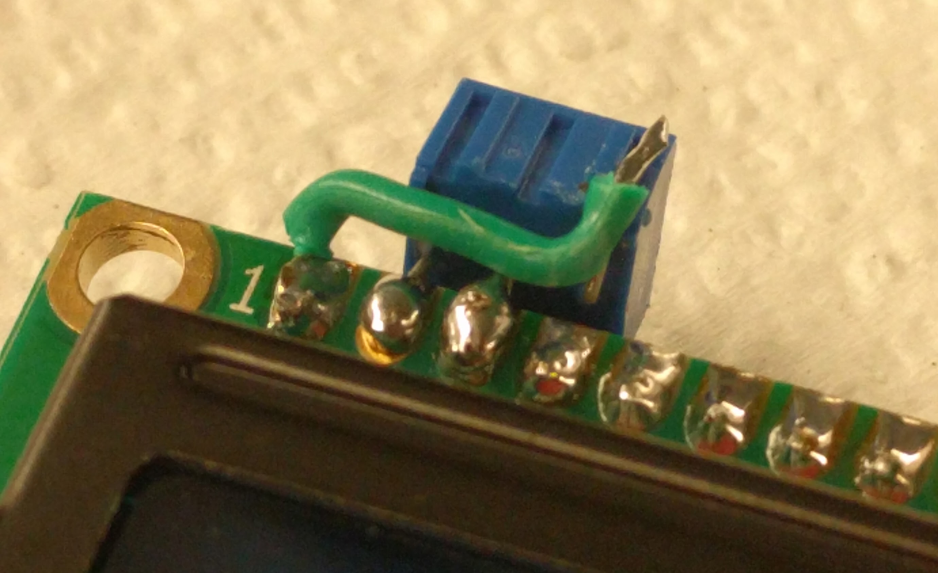
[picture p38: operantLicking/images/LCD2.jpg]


Connect the LCD to the RPi. Note you can use seven ribbon pins because the other end of the pins are next to each other on the RPi. You can adjust the potentiometer to obtain optimal contrast.   

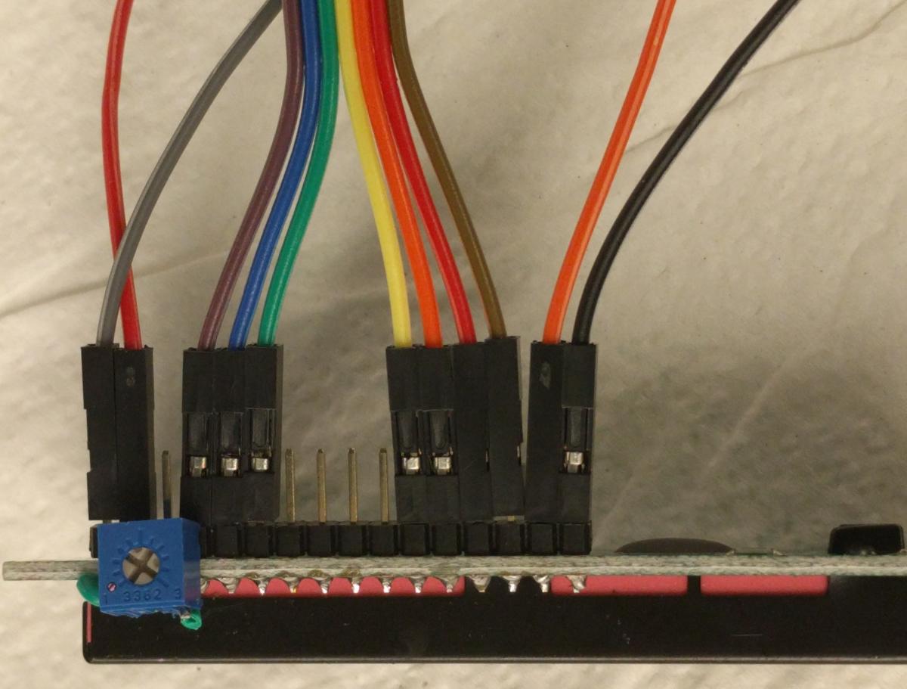
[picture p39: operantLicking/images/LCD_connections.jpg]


## Power

Connect two wires to a micro USB connector.

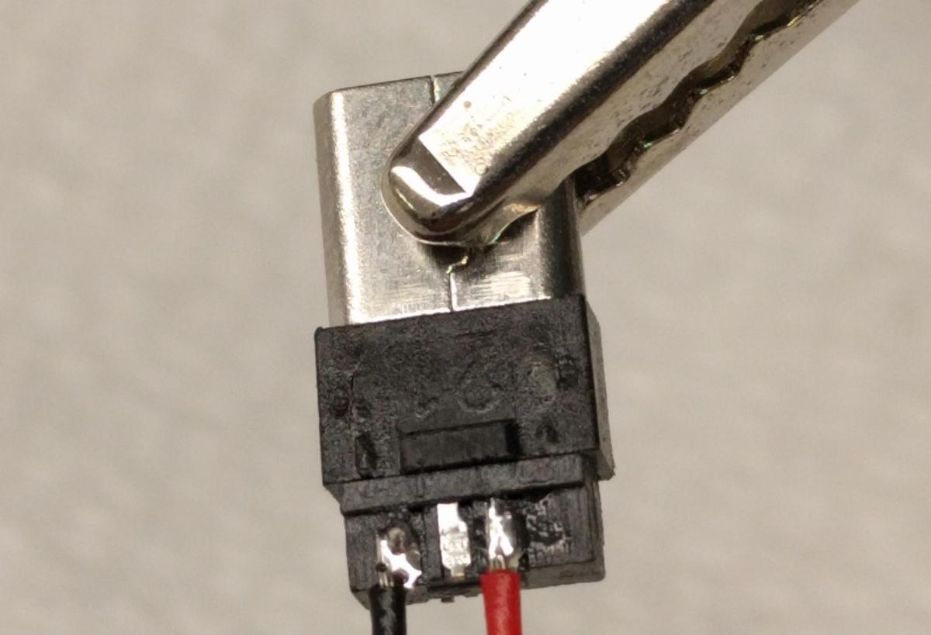
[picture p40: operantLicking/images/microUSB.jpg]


Cut the connector off a 12 V AC-DC converter (2 Amp). Connect the wires to the input side of a step down voltage converter. Connect the two wires from the micro USB connector to the output end (labeled on the back side of the board). Add two wires with female pins heads to the output side. These have 12 V and are connected to the stepper motor controller.  

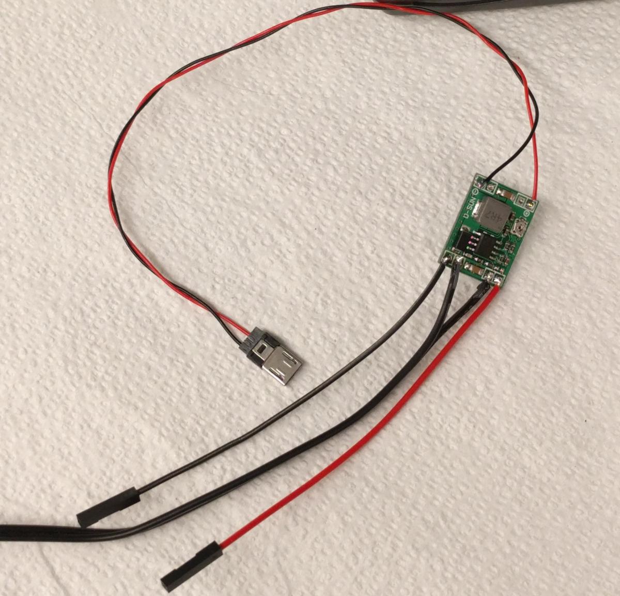
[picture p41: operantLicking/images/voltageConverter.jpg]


## Syringe pump

Insert a ball bearing into the 3D printed syringe end. 
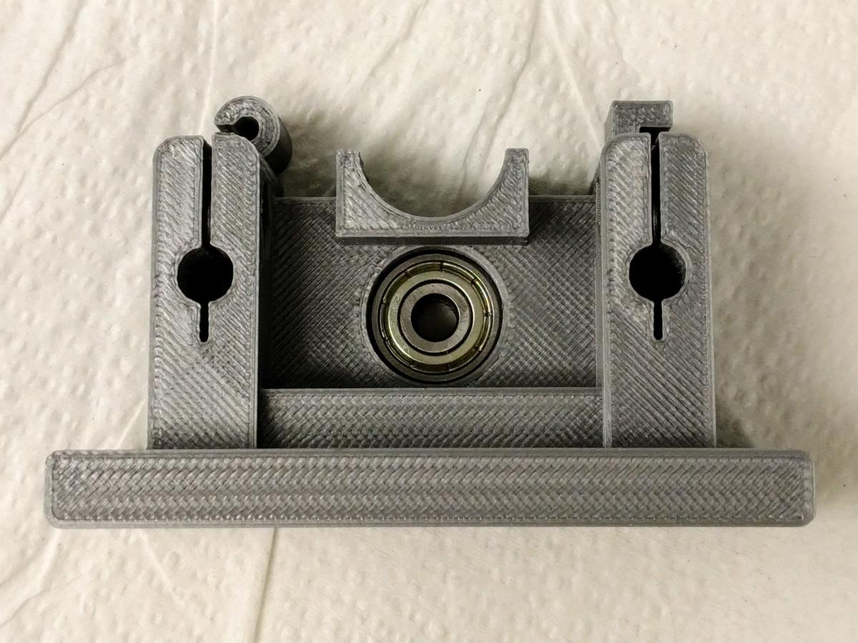
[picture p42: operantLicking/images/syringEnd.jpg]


Insert two linear bearings into the 3D printed syringe carrier. The syringe carrier must be printed precisely so that the linear bearing fit tightly alone its long axis but still has a little room to move in the other two dimensions. 

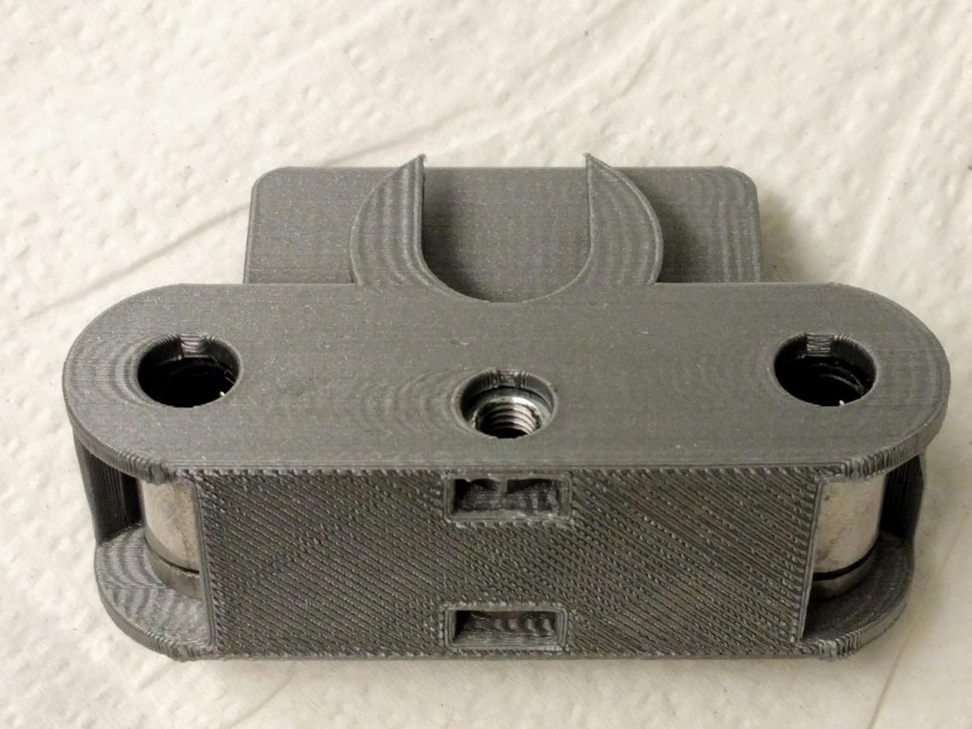
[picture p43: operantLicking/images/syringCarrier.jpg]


The step motor controller needs to have two wires added. One connects ENABLE and GROUND, the other connects VDD and REST. 

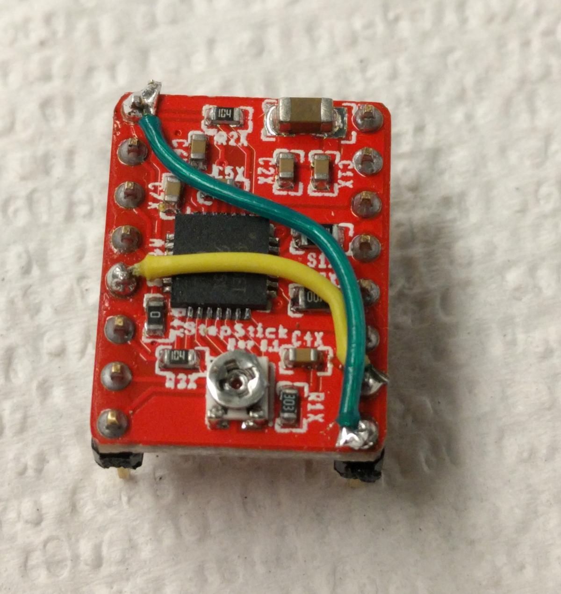
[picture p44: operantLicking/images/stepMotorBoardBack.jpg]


Extend the length of step motor connection wires to about 30 inches. Add female connection pins to the end of each wire. 

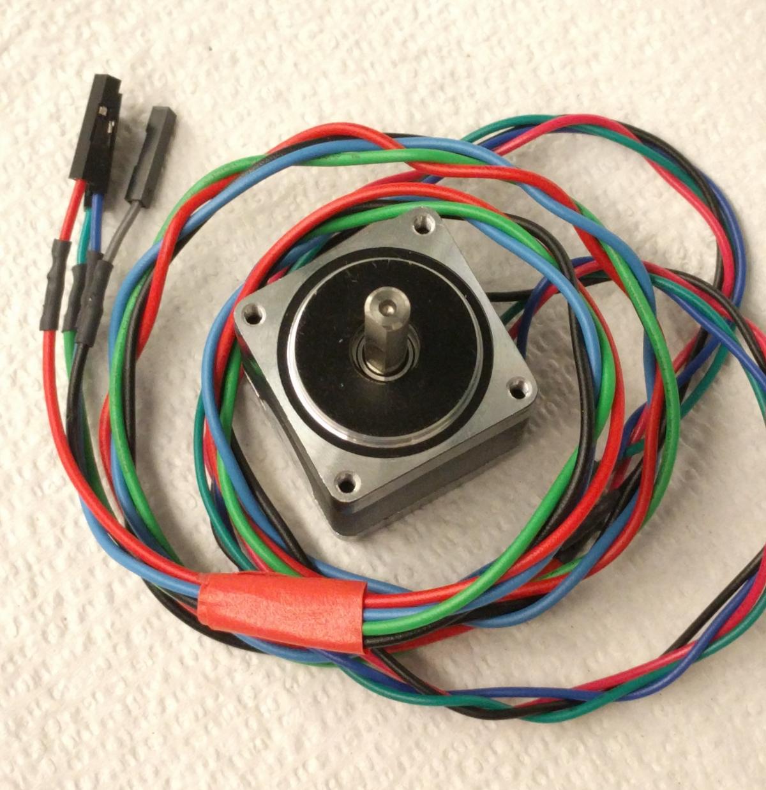
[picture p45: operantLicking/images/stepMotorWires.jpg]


A thin piece of copper is added to make it easier to fasten the threaded rod to the coupler .

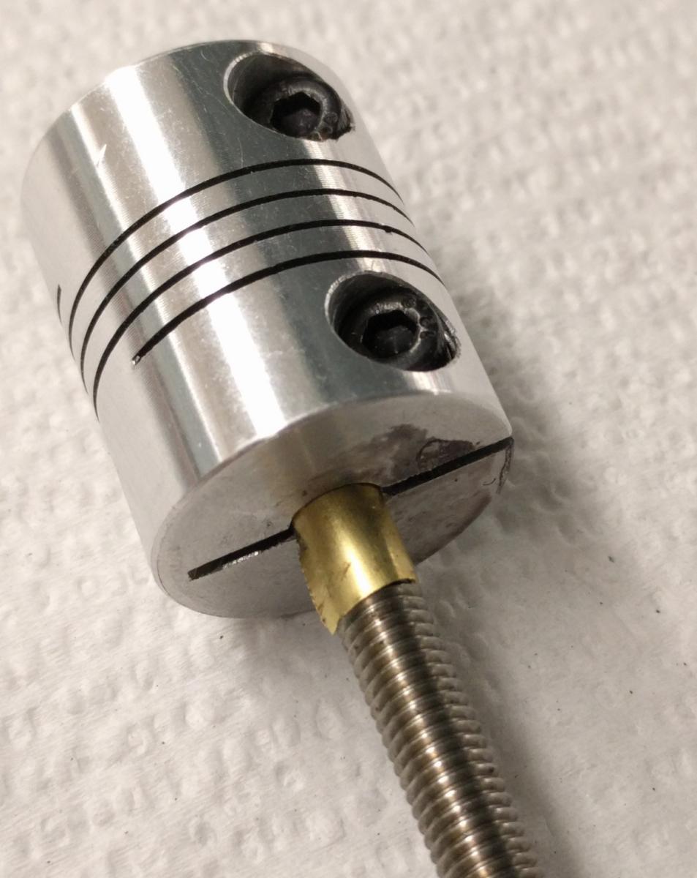
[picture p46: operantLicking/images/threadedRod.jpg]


The stepper motor is connected to a threaded rod via a coupler. 

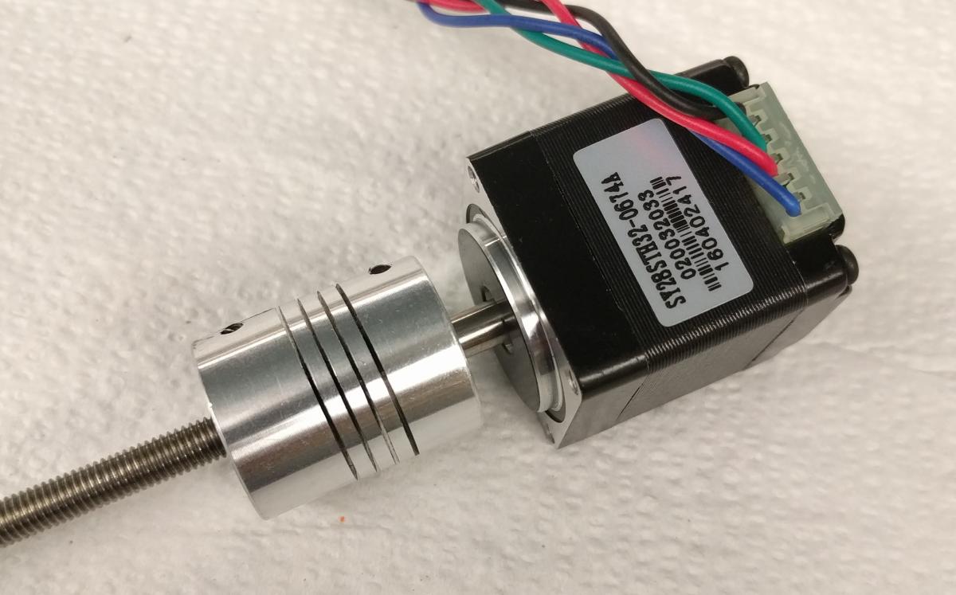
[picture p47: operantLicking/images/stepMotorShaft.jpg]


The fully assembled syringe pump.  (The stainless steel rods were cut into 5.5 inch segments.)

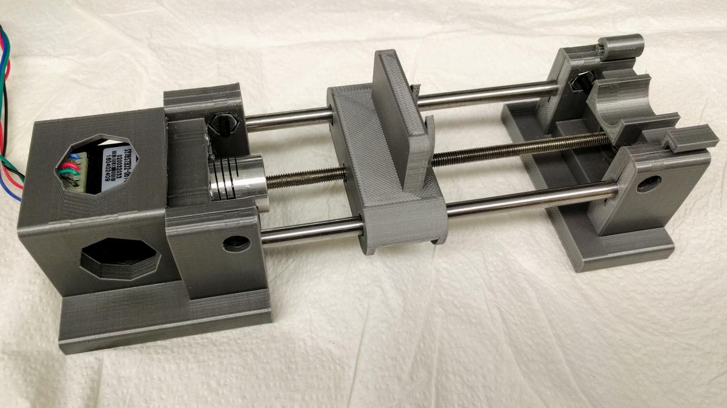
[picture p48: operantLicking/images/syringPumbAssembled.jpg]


## Final assembly

Print out a [RPi pin number label](../RPI.PinLables.pdf). Cut the middle grey area and put it around the pins on the RPi to help you identify the pins. Connect the parts following  the [ wiring table]  (wiring_tables.ods)
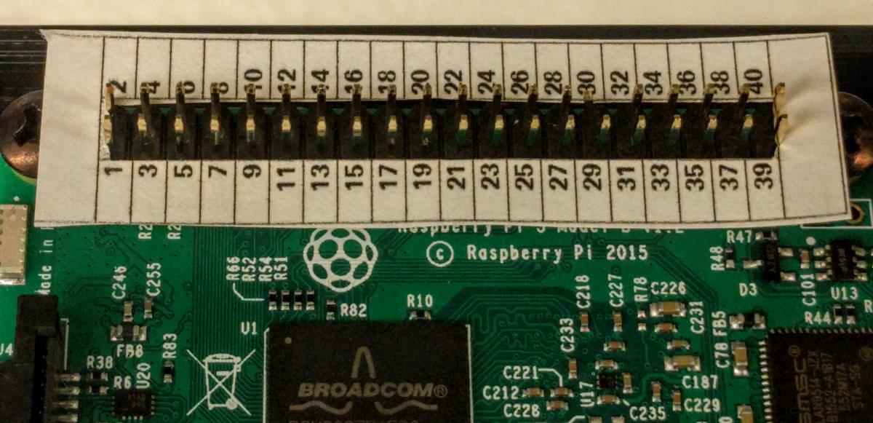
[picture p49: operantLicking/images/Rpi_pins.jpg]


All wires are connected.
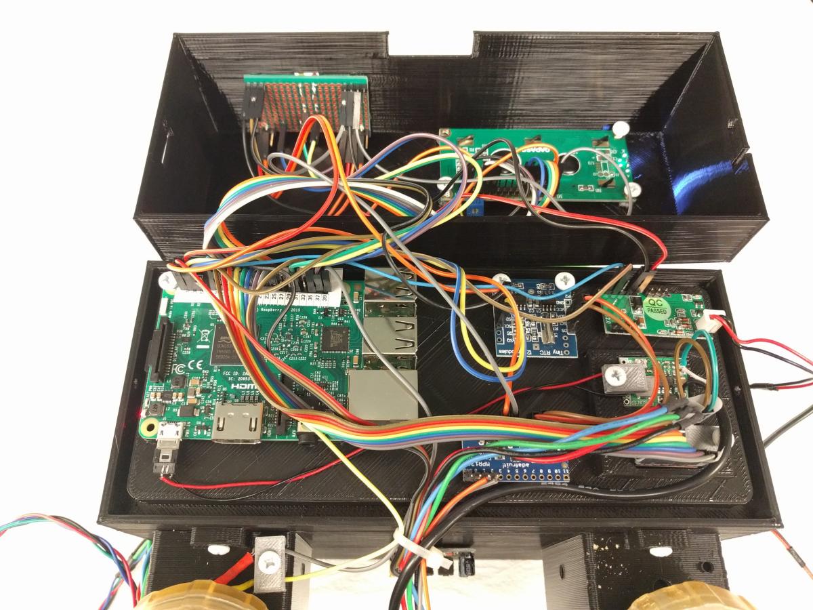
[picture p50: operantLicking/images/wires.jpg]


The fully assembled device. The RFID antenna can be placed on its holder on the right side.  The spouts can be disconnected for cleaning purpose. The LCD shows the following info:

*B07S14*: Box 7, session 14

*26A1*: the last four characters of the RFID

*54Le*: 54 minutes left

*a1i1r0vr10*: Active lick = 1, inactive lick = 1, reward = 0, Variable ratio 10 

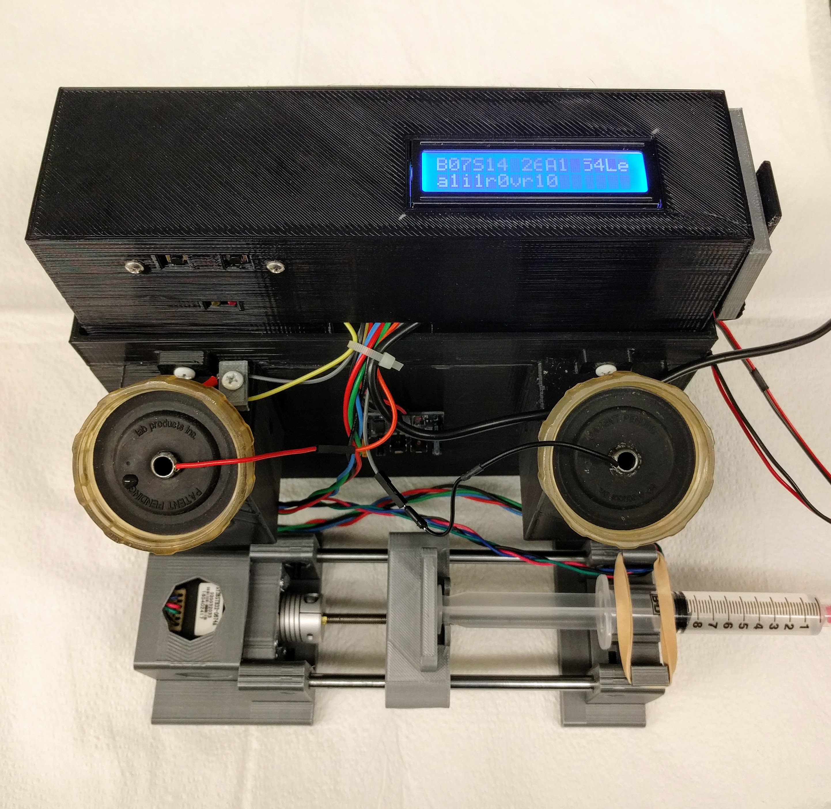
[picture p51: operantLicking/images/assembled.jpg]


A syringe is loaded in the pump. A rubber band is used to hold the syringe in place.  The pump can be placed on top of a rat cage.  The rest of the device can be placed inside the cage. Both spouts are connected. A PE tubing directs the liquid in the syringe to the active spout. 



The entire assembled device can be placed in the rat cage. A filtered cover  can be placed on the top (not shown). 
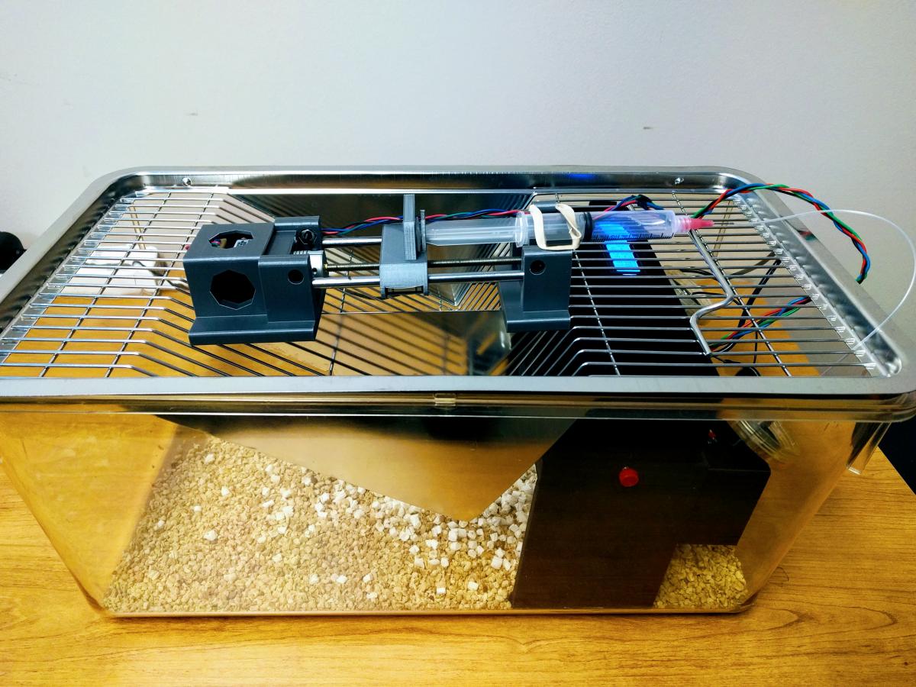
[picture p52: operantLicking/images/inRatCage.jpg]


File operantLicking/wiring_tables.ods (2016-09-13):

Raspberry Pi
GND touch | 39 | 40
switchboard | 37 | 38 | switchboard
OUT motion | 35 | 36
 | 33 | 34
motion LED on switch board | 31 | 32 | touch LED on switch board
 | 29 | 30 | grnd
 | 27 | 28
EN pump | 25 | 26 | LCD 14
MS1 pump | 23 | 24 | LCD 13
MS2 pump | 21 | 22 | LCD 12
MS3 pump | 19 | 20 | Cue -
RST pump | 17 | 18 | LCD 11
SLP pump | 15 | 16 | LCD 6
STEP pump | 13 | 14 | LCD 5
DIR pump | 11 | 12 | LCD 4
GRD motion | 9 | 10 | RFID 5
Cue + | 7 | 8 | RFID 4
SCL RTC | 5 | 6 | GRD RTC
SDA RTC | 3 | 4 | switchboard top row (positive)
Vin touch | 1 | 2 | VCC motion (5V)
RTC
P2 SCL | RP5
P2 SDA | RP3
P2 VCC | RP4
P2 GND | RP6
P1 SCL | Touch SCL
P1 SDA | Touch SDA
P1 VCC | switch board
P1 GND
Touch Sensor
SCL | RTC SCL
SDA | RTC SDA
GND | to switch board ground
VIN | Rpi pin 1
touch pin 1 | Active spout
touch pin 2 | Inactive spout
RFID
RFID 1 (next to pin holes) | switch board
RFID 2 | switch board
RFID 4 | RP8
RFID 5 | RP10
Motion Cue LED (green)
positive
Visual Cue LED
Positive | RP7
Negative | RP22
Motion sensor
OUT | RP35
GRD | RP9
VCC | RP2
Switch board
top row + | RTC VCC; RFID 1; LED power
bottom row - | RP30; RFID 2; LED grounds
RH resistor* | RP32
LH resistor* | RP33
RH switch* | RP38
LH switch* | RP37
Step motor
Enable | RP25
MS1 | RP23
MS2 | RP21
MS3 | RP19
RESET | RP17
SLEEP | RP15
STEP | RP13
DIRECT | RP11
1B* | motor (blue)
1A* | motor (red)
2A* | motor (green)
2B* | motor (black)
GND2 | pump power cord
VMOT2 | pump power cord
*note: connect GND and ENABLE on the back of the board
Connect RESET and VDD on the board

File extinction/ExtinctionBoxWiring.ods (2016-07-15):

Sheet: Sheet2
1 | 2 | 1 | 2 | 1 | 2 | 1 | 2 | 1 | 2 | 1 | 2 | 1 | 2
3 | 4 | 3 | 4 | 3 | 4 | 3 | 4 | 3 | 4 | 3 | 4 | 3 | 4
5 | 6 | 5 | 6 | 5 | 6 | 5 | 6 | 5 | 6 | 5 | 6 | 5 | 6
7 | 8 | 7 | 8 | 7 | 8 | 7 | 8 | 7 | 8 | 7 | 8 | 7 | 8
9 | 10 | 9 | 10 | 9 | 10 | 9 | 10 | 9 | 10 | 9 | 10 | 9 | 10
11 | 12 | 11 | 12 | 11 | 12 | 11 | 12 | 11 | 12 | 11 | 12 | 11 | 12
13 | 14 | 13 | 14 | 13 | 14 | 13 | 14 | 13 | 14 | 13 | 14 | 13 | 14
15 | 16 | 15 | 16 | 15 | 16 | 15 | 16 | 15 | 16 | 15 | 16 | 15 | 16
17 | 18 | 17 | 18 | 17 | 18 | 17 | 18 | 17 | 18 | 17 | 18 | 17 | 18
19 | 20 | 19 | 20 | 19 | 20 | 19 | 20 | 19 | 20 | 19 | 20 | 19 | 20
21 | 22 | 21 | 22 | 21 | 22 | 21 | 22 | 21 | 22 | 21 | 22 | 21 | 22
23 | 24 | 23 | 24 | 23 | 24 | 23 | 24 | 23 | 24 | 23 | 24 | 23 | 24
25 | 26 | 25 | 26 | 25 | 26 | 25 | 26 | 25 | 26 | 25 | 26 | 25 | 26
27 | 28 | 27 | 28 | 27 | 28 | 27 | 28 | 27 | 28 | 27 | 28 | 27 | 28
29 | 30 | 29 | 30 | 29 | 30 | 29 | 30 | 29 | 30 | 29 | 30 | 29 | 30
31 | 32 | 31 | 32 | 31 | 32 | 31 | 32 | 31 | 32 | 31 | 32 | 31 | 32
33 | 34 | 33 | 34 | 33 | 34 | 33 | 34 | 33 | 34 | 33 | 34 | 33 | 34
35 | 36 | 35 | 36 | 35 | 36 | 35 | 36 | 35 | 36 | 35 | 36 | 35 | 36
37 | 38 | 37 | 38 | 37 | 38 | 37 | 38 | 37 | 38 | 37 | 38 | 37 | 38
39 | 40 | 39 | 40 | 39 | 40 | 39 | 40 | 39 | 40 | 39 | 40 | 39 | 40
col height =0.10 in
Center col width=0.20 in
cut the grey part out and lay it over your GPIO pins

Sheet: Sheet1
Extinction box wiring diagram
Hao Chen | 07/15/16
 |  | GPIO.Board
 | touch sensor 3v | 1 | 2 | LCD pin 15
 | touch sensor sda | 3 | 4 | LCD pin 2
 | touch sensor scl | 5 | 6 | LCD pin 1
 |  | 7 | 8
 | touch sensor gnd | 9 | 10
 | LCD pin 12 | 11 | 12
 |  | 13 | 14
 | LCD pin 14 | 15 | 16 | LCD pin 11
 |  | 17 | 18 | LCD pin 6
 |  | 19 | 20 | LCD pin 5
 |  | 21 | 22 | LCD pin 4
 |  | 23 | 24
 |  | 25 | 26
 |  | 27 | 28
 | LED1 + | 29 | 30 | LED1 -
 |  | 31 | 32
 | LED2 - | 33 | 34 | LED2 +
 |  | 35 | 36
 |  | 37 | 38
 | LCD pin 5 | 39 | 40 | LCD pin 13
 | LCD pin 3 is connected to the middle wire of the potentiometer
 | the other two pins of the potential meter are connected to LCD
 | Pins 1 and 2. position does not matter
 | The two LEDs are the cue lights.

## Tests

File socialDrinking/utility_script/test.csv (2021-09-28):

00001450 | 2020-11-21 | 19:13:43 | BOX_1 | 262 | vr10TO10 | 57600 | 0 | 0 | 0 | 0 | 0 | 0
3b9ad14d | 2020-11-21 | 19:13:43 | BOX_1 | 262 | vr10TO10 | 57600 | 14893 | 22 | 160 | 0 | 352 | 42
ratUnknown | 2020-11-21 | 19:13:43 | BOX_1 | 262 | vr10TO10 | 57600 | 6 | 0 | 0 | 0
00001450 | 2020-11-21 | 19:16:17 | BOX_2 | 155 | vr10TO10 | 57600 | 0 | 0 | 0 | 0 | 3 | 0
3b9ad12b | 2020-11-21 | 19:16:17 | BOX_2 | 155 | vr10TO10 | 57600 | 20 | 0 | 2 | 0 | 44 | 28
ratUnknown | 2020-11-21 | 19:16:17 | BOX_2 | 155 | vr10TO10 | 57600 | 25 | 0 | 0 | 0
00001450 | 2020-11-21 | 19:16:48 | BOX_3 | 162 | vr10TO10 | 57600 | 0 | 0 | 0 | 0 | 0 | 0
3b9ad166 | 2020-11-21 | 19:16:48 | BOX_3 | 162 | vr10TO10 | 57600 | 7821 | 115 | 96 | 0 | 76 | 54
ratUnknown | 2020-11-21 | 19:16:48 | BOX_3 | 162 | vr10TO10 | 57600 | 1725 | 266 | 0 | 0
00001450 | 2020-11-21 | 19:20:29 | BOX_4 | 203 | vr10TO10 | 57600 | 0 | 0 | 0 | 0 | 0 | 0
3b9ad007 | 2020-11-21 | 19:20:29 | BOX_4 | 203 | vr10TO10 | 57600 | 13094 | 172 | 210 | 12731 | 256 | 55
ratUnknown | 2020-11-21 | 19:20:29 | BOX_4 | 203 | vr10TO10 | 57600 | 166 | 0 | 0 | 166
00001450 | 2020-11-21 | 19:20:04 | BOX_5 | 216 | vr10TO10 | 57600 | 0 | 0 | 0 | 0 | 0 | 0
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

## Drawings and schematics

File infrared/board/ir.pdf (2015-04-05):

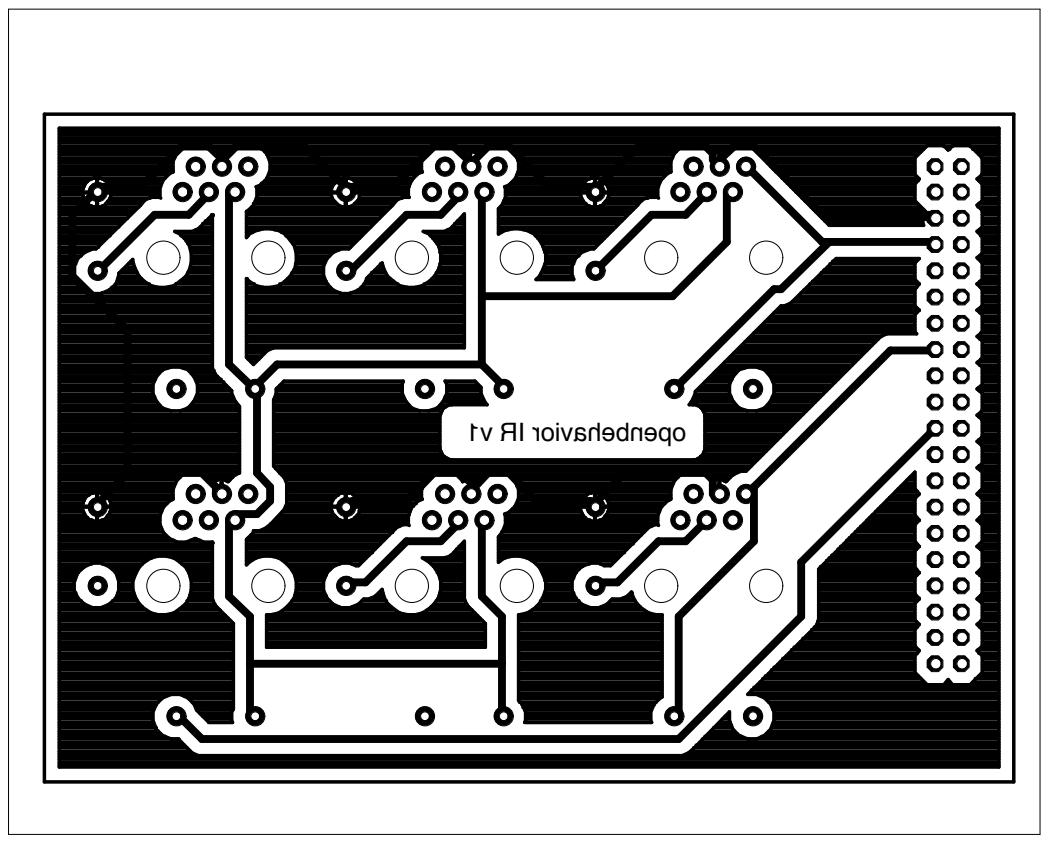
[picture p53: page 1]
openbehavior IR v1

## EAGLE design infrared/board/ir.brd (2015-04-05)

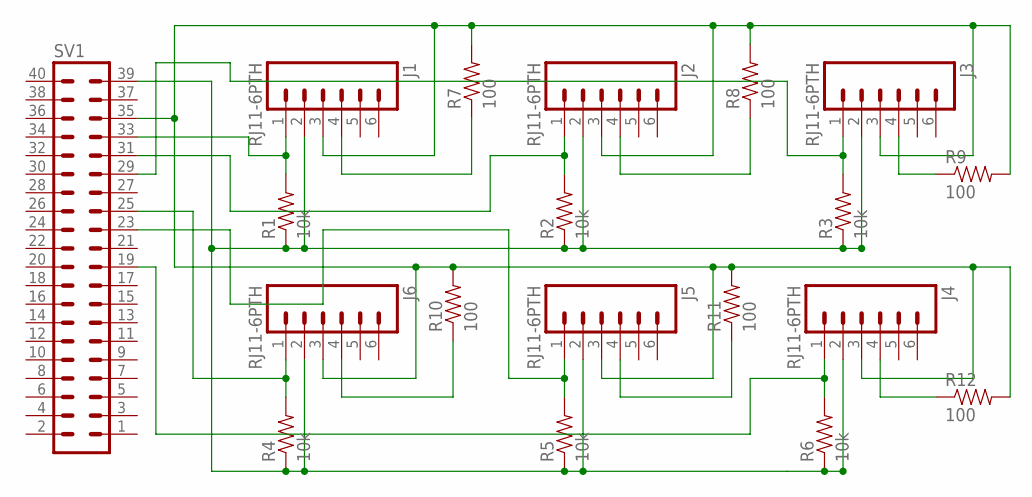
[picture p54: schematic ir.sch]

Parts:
J1, J2, J3, J4, J5, J6: RJ11-6PTH; RJ11-6
R1, R2, R3, R4, R5, R6: 10k; AXIAL-0.3
R7, R8, R9, R10, R11, R12: 100; AXIAL-0.3
SV1: MA20-2

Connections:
unnamed: J1.2, J2.2, J3.2, J4.2, J5.2, J6.2, R1.P$1 (1), R2.P$1 (1), R3.P$1 (1), R4.P$1 (1), R5.P$1 (1), R6.P$1 (1), SV1.39
unnamed: J2.1, R2.P$2 (2), SV1.31
unnamed: J3.1, R3.P$2 (2), SV1.29
unnamed: J6.1, R4.P$2 (2), SV1.25
unnamed: J5.1, R5.P$2 (2), SV1.23
unnamed: J4.1, R6.P$2 (2), SV1.19
unnamed: J1.1, R1.P$2 (2), SV1.33
unnamed: J1.3, J2.3, J3.3, J4.3, J5.3, J6.3, R7.P$2 (2), R8.P$2 (2), R9.P$2 (2), R10.P$2 (2), R11.P$2 (2), R12.P$2 (2), SV1.35
unnamed: J1.4, R7.P$1 (1)
unnamed: J2.4, R8.P$1 (1)
unnamed: J3.4, R9.P$1 (1)
unnamed: J6.4, R10.P$1 (1)
unnamed: J5.4, R11.P$1 (1)
unnamed: J4.4, R12.P$1 (1)

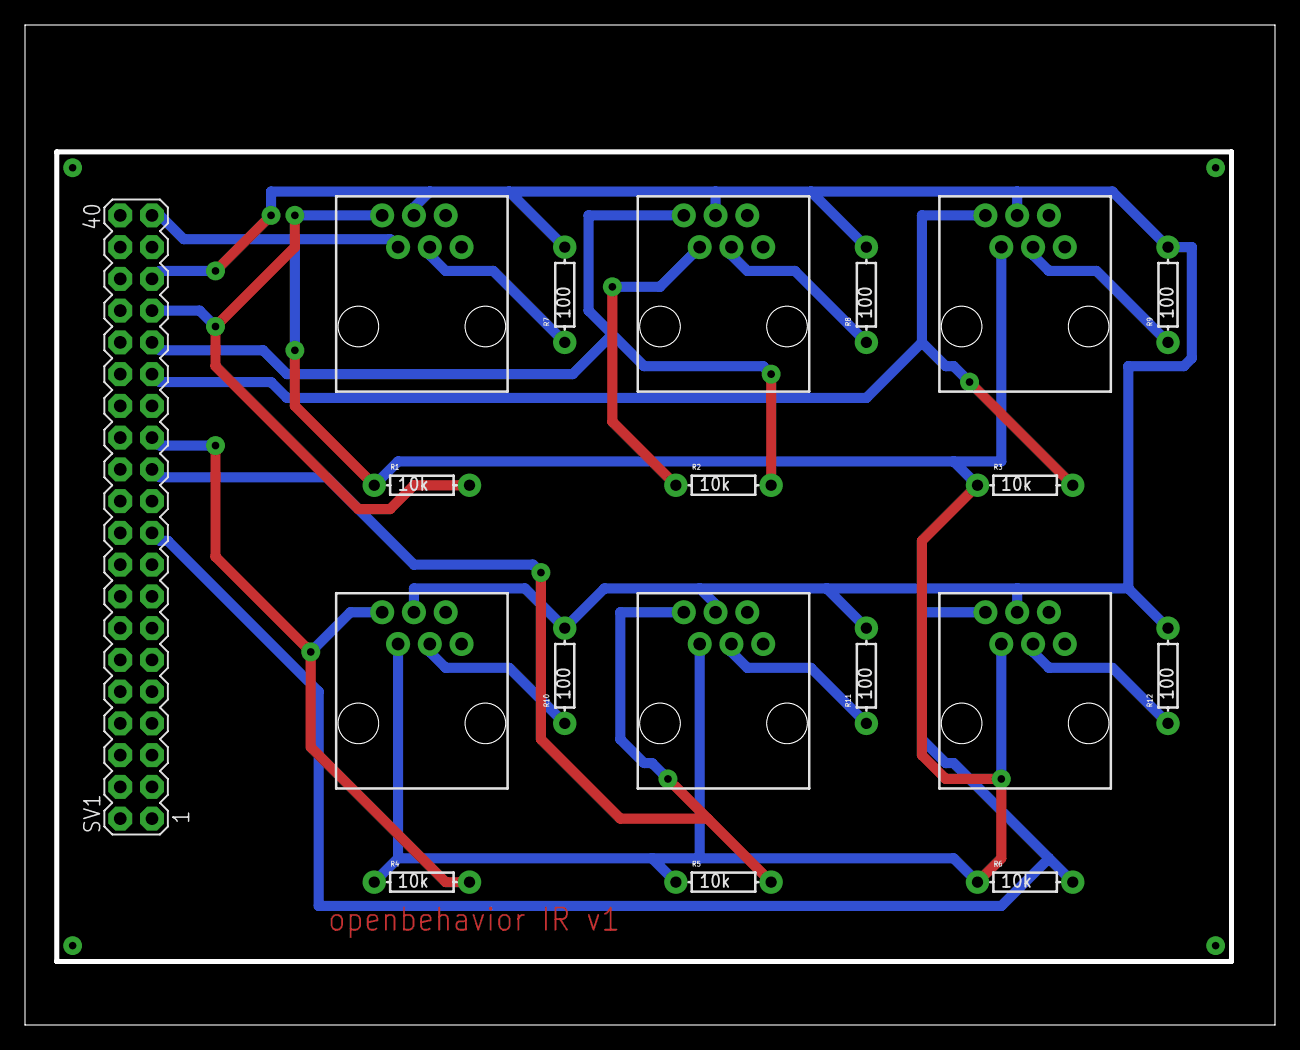
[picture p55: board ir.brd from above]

Board: 2 copper layers, 100.0 x 80.0 mm, 19 parts (0 on the bottom side), 14 nets.

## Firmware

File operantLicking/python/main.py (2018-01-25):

#!/usr/bin/python

# Copyright 2016 University of Tennessee Health Sciences Center
# Author: Matthew Longley <mlongle1@uthsc.edu>
# Author: Hao Chen <hchen@uthsc.edu>
#
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
# BEGIN IMPORT PRELUDE
import sys
import getopt
import time
from threading import Timer
import subprocess32 as subprocess
import RPi.GPIO as gpio
import Adafruit_MPR121.MPR121 as MPR121
import pumpcontrol
import serial
import touchsensor
import datalogger
import os
import random
import Adafruit_CharLCD as LCD
# END IMPORT PRELUDE


def initLCD():
    # Raspberry Pi pin configuration:
    lcd_rs        = 18  # RPi PIN 12 // LCD pin 4 
                        # RPi PIN 14 // LCD pin 5 
    lcd_en        = 23  # RPi PIN 16 // LCD pin 6
    lcd_d4        = 24  # RPi PIN 18 // LCD pin 11
    lcd_d5        = 25  # RPi PIN 22 // LCD pin 12
    lcd_d6        =  8  # RPi PIN 24 // LCD pin 13
    lcd_d7        =  7  # RPi PIN 26 // LCD pin 14
    lcd_backlight =  4 
    # Define LCD column and row size for 16x2 LCD.
    lcd_columns = 16
    lcd_rows    =  2
    # Initialize the LCD using the pins above.
    lcd = LCD.Adafruit_CharLCD(lcd_rs, lcd_en, lcd_d4, lcd_d5, lcd_d6, lcd_d7, lcd_columns, lcd_rows, lcd_backlight)
    lcd.clear()
    return lcd 

def mesg(m):
    lcd.clear()
    lcd.message(m) 

def printUsage():
    print(sys.argv[0] + ' -t <timeout> -f <fixed ratio>')
    
def resetPumpTimeout():
    global pumptimedout
    pumptimedout = False

def blinkTouchLED(duration):
    gpio.output(TOUCHLED, gpio.HIGH)
    time.sleep(duration)
    gpio.output(TOUCHLED, gpio.LOW)

def ReadRFID(path_to_sensor) :
    baud_rate = 9600 
    time_out = 0.05
    uart = serial.Serial(path_to_sensor, baud_rate, timeout = time_out)
    uart.close()
    uart.open()
    uart.flushInput()
    uart.flushOutput()
    print(path_to_sensor + " initiated")
    Startflag = "\x02"
    Endflag = "\x03"
    while True:
        Z = 0
        Tag = 0
        ID = ""
        Z = uart.read()
        if Z == Startflag:
            for Counter in range(13):
                Z = uart.read()
                ID = ID + str(Z)
            ID = ID.replace(Endflag, "" ) 
            if int(ID, 16) != 0:
                #if len(ID) > 12:
                #    ID=ID[-12:]
                print ("RFID  detected: "+ ID)
                return (ID)

# BEGIN CONSTANT DEFINITIONS
TIR = int(16) # Pin 36
SW1 = int(26) # Pin 37
SW2 = int(20) # Pin 38
TOUCHLED = int(12) #pin 32
MOTIONLED= int(6) #pin 31
# END CONSTANT DEFINITIONS

# BEGIN GLOBAL VARIABLES
interLickInterval=1 # second
logged={}
touchcounter = 0
pumptimedout = False
act=0 # number of licks on the active spout
ina=0 # number of licks on the inactive spout
rew=0 # number of reward
wat=0 # number of licks on water spout
lapsed=0  # time since program start
updateTime=0 # time since last LCD update
vreinstate=0
# ENG GLOBAL VARIABLES

# Initialize GPIO
gpio.setwarnings(False)
gpio.setmode(gpio.BCM)

# Setup switch pins
gpio.setup(SW1, gpio.IN, pull_up_down=gpio.PUD_DOWN)
gpio.setup(SW2, gpio.IN, pull_up_down=gpio.PUD_DOWN)
gpio.setup(TIR, gpio.IN, pull_up_down=gpio.PUD_DOWN)
gpio.setup(TOUCHLED, gpio.OUT)
gpio.setup(MOTIONLED, gpio.OUT)

# initiate LCD
lcd=initLCD()
#mesg("Prog. Started")

# Initialize pump
pump = pumpcontrol.Pump(gpio)

# enable the switches to move the pump
subprocess.call("sudo python /home/pi/openbehavior/operantLicking/python/pumpmove.py" + " &", shell=True)

# Run the deviceinfo script
mesg("Hurry up, Wifi!")
os.system("/home/pi/openbehavior/wifi-network/deviceinfo.sh")

# Initialize touch sensor
tsensor = touchsensor.TouchSensor()

# turn lights on to indicate ready to run
gpio.output(TOUCHLED, gpio.HIGH)
gpio.output(MOTIONLED, gpio.HIGH)

# device id
dId=open("/home/pi/deviceid")
deviceId=dId.read().strip()

# wait for RFID scanner to get RatID
datetime=time.strftime("%Y-%m-%d %H:%M:%S", time.localtime())
mesg("Pls scan RFID VR10\n"+datetime)
RatID=ReadRFID("/dev/ttyAMA0")

# the default schedule is vr10 timeout20. Other reinforcemnt schedules can be started by using RFIDs.
if RatID=="1E003E3B0C17" or RatID=="2E90EDD235B4":
    schedule="pr"
    breakpoint=2.0
    timeout = 20
    nextratio=int(5*2.72**(breakpoint/5)-5)
    sessionLength=10*60 # session ends after 10 min inactivity
    ratio=""
    mesg("Run PR Schedule.\nPls Scan Rat")
    time.sleep(3)
    RatID=ReadRFID("/dev/ttyAMA0")
    #signal motion sensor to keep recording until this is changed
    with open ("/home/pi/prend", "w") as f:
        f.write("no")
elif RatID=="2E90EDD079FA" or RatID=="2E90EDD071F2":
    schedule="fr"
    ratio = 2
    timeout =  20
    sessionLength=60*60*1 # one hour assay
    nextratio=ratio
    mesg("Run FR"+str(ratio)+" Prog.\nPls Scan Rat")
    time.sleep(3)
    RatID=ReadRFID("/dev/ttyAMA0")
elif RatID=="2E90EDD20283" or RatID=="2E90EDD226A7":
    schedule="ext"
    timeout=0
    ratio=1000000
    nextratio=1000000
    sessionLength=60*60*1
    mesg("Run Ext"+str(ratio)+" Prog.\nPls Scan Rat")
    time.sleep(3)
    RatID=ReadRFID("/dev/ttyAMA0")
elif RatID=="2E90EDD21796":
    schedule="vr"
    ratio = 10
    timeout =  20
    sessionLength=60*60*22 # twenty two hour assay
    nextratio=ratio
    mesg("Run VR"+str(ratio)+"22h\nPls Scan Rat")
    time.sleep(3)
    RatID=ReadRFID("/dev/ttyAMA0")
elif RatID=="0400F16C5DC4":
    vreinstate=1
    schedule="vr"
    ratio = 5 
    timeout = 1 
    sessionLength=60*60*1 # one hour assay
    nextratio=ratio
    mesg("Run VREINST\n"+"Pls Scan Rat")
    time.sleep(3)
    RatID=ReadRFID("/dev/ttyAMA0")
else: # vr
    schedule="vr"
    ratio=10
    nextratio=ratio
    timeout = 20
    sessionLength=60*60*1 # one hour assay

mesg("RatID: "+ RatID)
print (RatID)

#turn lights off to indicate RFID recieved
mesg("Session Started")
gpio.output(TOUCHLED, gpio.LOW)
gpio.output(MOTIONLED, gpio.LOW)

# session id 
with open ("/home/pi/sessionid", "r+") as f:
    storedSessionID=f.read().strip()
    sessionID=int(storedSessionID)+1  
    f.seek(0)
    f.write(str(sessionID))
    f.close()

# start motion sensor Note: motion sensor needs to be started before session ID is incremented
# print ("staring motion sensor")
subprocess.call("sudo python /home/pi/openbehavior/operantLicking/python/motion.py " +  " -SessionLength " + str(sessionLength) + " -RatID " + RatID +  " -Schedule " + schedule + " &", shell=True)

# Initialize data logger 
dlogger = datalogger.LickLogger()
dlogger.createDataFile(RatID, schedule+str(ratio)+'TO'+str(timeout))

# Get start time
sTime = time.time()
lastActiveLick=sTime
lastInactiveLick=sTime

def showdata():
    if schedule=='pr':
        minsLeft=int((sessionLength-(time.time()-lastActiveLick))/60)
    else:
        minsLeft=int((sessionLength-lapsed)/60)
    mesg("B" + deviceId[-2:]+  "S"+str(sessionID) + " " + RatID[-4:] + " " + str(minsLeft) + "Left\n"+ "a" + str(act)+"i"+str(ina) + "r" +  str(rew) + schedule + str(nextratio))
    return time.time()


if (vreinstate):
    subprocess.call('python /home/pi/openbehavior/operantLicking/python/blinkenlights.py -times 10 &', shell=True)

while lapsed < sessionLength:
    time.sleep(0.05) # set delay to adjust sensitivity of the sensor.
    lapsed = time.time() - sTime
    i = tsensor.readPinTouched()
    if i == 1:
        thisActiveLick=time.time() 
        print ("act=" + str(act) +  " rew= "+str(rew)+" nextratio=" + str(nextratio)+" counter="+str(touchcounter))
        # only count licks that are within interlick interval to exclude noise
        # need to deal with not skipping the first lick in a series
        if thisActiveLick-lastActiveLick < interLickInterval: # rat licks in rapid sucsession
            #print ("this one counts, timeout?", str(pumptimedout))
            if (lastActiveLick not in logged): 
                act+=1
                dlogger.logEvent("ACTIVE", lastActiveLick-sTime)
            act+=1
            dlogger.logEvent("ACTIVE", lapsed)
            blinkTouchLED(0.02)
            if not pumptimedout:
                touchcounter += 1
                if (lastActiveLick not in logged):
                    touchcounter += 1
                if touchcounter >= nextratio:
                    rew+=1
                    updateTime=showdata()
                    dlogger.logEvent("REWARD", lapsed, nextratio)
                    touchcounter = 0
                    pumptimedout = True
                    pumpTimer = Timer(timeout, resetPumpTimeout)
                    pumpTimer.start()
                    subprocess.call('python /home/pi/openbehavior/operantLicking/python/blinkenlights.py &', shell=True)
                    pump.move(0.08) # This is 60ul
                    if schedule == "fr":
                        nextratio=ratio
                    elif schedule == "vr":
                        nextratio=random.randint(1,ratio*2)
                    elif schedule == "pr":
                        breakpoint+=1.0
                        nextratio=int(5*2.72**(breakpoint/5)-5)
                else:
                    updateTime=showdata()
#           logged[lastActiveLick]=1
            logged[thisActiveLick]=1
        lastActiveLick=thisActiveLick
    elif i == 2:
        thisInactiveLick=time.time() 
        # only count licks that are within interlick interval to exclude noise
        # need to deal with not skipping the first lick in a series
        if thisInactiveLick-lastInactiveLick < interLickInterval: # rat licks in rapid sucsession
            if (lastInactiveLick not in logged): 
                ina+=1
                dlogger.logEvent("INACTIVE", lastInactiveLick-sTime)
            ina+=1
            dlogger.logEvent("INACTIVE", lapsed)
            blinkTouchLED(0.02)
            logged[thisInactiveLick]=1
        lastInactiveLick=thisInactiveLick
        blinkTouchLED(0.05)
        updateTime=showdata()
#    elif i == 0:
#        wat+=1
#        dlogger.logEvent("WATER", lapsed)
#        blinkTouchLED(0.05)
#        updateTime=showdata()
    elif time.time() - updateTime > 60:
        updateTime=showdata()
    # keep this here so that the PR data file will record lapse from sesion start 
    if schedule=="pr":
        lapsed = time.time() - lastActiveLick 
#        print ("prlaps", lapsed)
 
# signal the motion script to stop recording
if schedule=='pr':
    with open("/home/pi/prend", "w") as f:
        f.write("yes")

dlogger.logEvent("SessionEnd", time.time()-sTime)

mesg("B" + deviceId[-2:]+  "S"+str(sessionID) + " " + RatID[-4:] + " Done!\n" + "a" + str(act)+"i"+str(ina) + "r" +  str(rew)) 

subprocess.call('/home/pi/openbehavior/wifi-network/rsync.sh &', shell=True)

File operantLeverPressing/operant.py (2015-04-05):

#!/usr/bin/python

import RPi.GPIO as GPIO

import time
from time import gmtime, strftime, sleep
import picamera
import os
import sys
import getopt
import subprocess
import signal


## all  times are in seconds

# GPIO setup.   
pump=7 # syringe pump
l1=8 # active lever 
l2=10  # inactive lever
light=16 # cue light

def init():
        GPIO.setmode(GPIO.BOARD)
        GPIO.setwarnings(False)
        GPIO.setup(pump, GPIO.OUT)  #for syringe pump
        GPIO.setup(l1, GPIO.IN)  #for active lever (i.e., lever 1)
        GPIO.setup(l2, GPIO.IN)  #for inactive lever (i.e., lever 2)
        GPIO.setup(light, GPIO.OUT)  #for light

def main(argv):
        fixedR=5  # fixed ratio
        injectT=5  # the time for which the pump will run, based on the weight of the mouse
        timeout = 10 # nothing will happen on lever presses
        sessionT = 300 # session time will be overwritten by the parameter provided at the command line   
        c1=0 # counter for lever 1  
        c2=0 # counter for lever 2 
        i1=0 # counter for lever 1 during injection
        i2=0 # counter for lever 2 during injection
        t1=0 # counter for lever 1 during timeout
        t2=0 # counter for lever 2 during timeout
        animalID = "animal ID"
        camera = picamera.PiCamera()
        camera.resolution = (320,240)
        try:
                opts, args = getopt.getopt(sys.argv[1:],"hf:i:t:s:a:",["fr","injectTime", "timeout", "sessionT", "animalID"])
        except getopt.GetoptError:
                print("sudo python3 operant.py -f <fixedRatio> -i <injectTime> -t <timeout> -s <sessionTime> -a <animalID>")
                sys.exit(2)
        for opt, arg in opts:
                if opt == '-h':
                        print("sudo python3 operant.py -f <fixedRatio> -i <injectTime> -t <timeout> -s <sessionTime> -a <animalID>")
                        sys.exit()
                elif opt in ("-f", "--fr"):
                        fixedR = arg
                elif opt in ("-i", "--injectTime"):
                        injectT = arg
                elif opt in("-t", "--timeout"):
                        timeout = arg
                elif opt in("-s", "--sessionT"):
                        if(int(arg)>=300):
                                sessionT=arg
                elif opt in("-a", "--animalID"):
                        animalID = arg
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

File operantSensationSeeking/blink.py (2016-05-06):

#!/usr/bin/env python2

import RPi.GPIO as gpio
import time
import random
import argparse

parser=argparse.ArgumentParser()
parser.add_argument('-datafile',  type=str)
parser.add_argument('-start',  type=float)
parser.add_argument('-RatID',  type=str)
parser.add_argument('-interval',  type=int)
args=parser.parse_args()
print ("\n")
print ("\n")
print (args.datafile)
print (args.RatID)
print (args.start )
print ("\n")

idfile=open("/home/pi/deviceid")
boxid=idfile.read()
boxid=boxid.strip()

# green and red LEDs are for sensation seeking
greenLed=7
redLed=11
houseLight1=33
houseLight2=37
pins=[greenLed,redLed]

gpio.setmode(gpio.BOARD)
gpio.setwarnings(False)
gpio.setup(greenLed, gpio.OUT)
gpio.setup(redLed, gpio.OUT)
gpio.setup(houseLight1, gpio.OUT)
gpio.setup(houseLight2, gpio.OUT)

## blinks the green LED and/or red LED at a randomly selected frequency for a randomly selected time period, repeat 1-3 times
def blink(pins):
	whichpin=random.randint(0,3)
	if whichpin==0:
		pin=[pins[0]]
		Pin="Red"
	elif whichpin==1:
		pin=[pins[1]]
		Pin="Green"
	elif whichpin==2:
		pin=pins
		Pin="Both"
	else:
		pin=[pins[0],pins[1],9] # 9 = blink alternatively 
		Pin="Alt."
	numTimes=random.randint(1,3)
	speed=random.randint(1,9)/float(9)
	lapsed=time.time()-args.start
	# which house light to turn off?
	hL=1
	if random.randint(0,9)< 5 :
		hL=0
		print "blink house lights"
		for i in range (0, random.randint(2,4)):
			print (str(i))
			gpio.output(houseLight1,False)
			gpio.output(houseLight2,False)
			time.sleep(random.randint(1,4)/float(8))
			gpio.output(houseLight1,True)
			gpio.output(houseLight2,True)
			time.sleep(random.randint(1,4)/float(8))
	if len(pin)==3:
		print ("blink pins alternately "+str(pin)+" for "+str(numTimes)+" times at "+str(speed) + " speed") 
		for i in range(0,numTimes):
			gpio.output(pin[0],True)
			time.sleep(speed)
			gpio.output(pin[0],False)
			gpio.output(pin[1],True)
			time.sleep(speed)
			gpio.output(pin[1],False)
			time.sleep(speed)
	elif len(pin)==2:
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

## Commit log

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2015-02-11 added EAGLE PCB files
    [ir.GBL, ir.GBO, ir.GBS, ir.GTL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]
2015-02-12 upload sample data
    [sampleData.csv]
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2015-03-17 Added setup scripts for DS-1307 Real Time Clock and Setup Scripts for MCP9808 Temperature Sensor
    [temperature.csv]
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2015-10-23 starting to add 3D files
    [ratButton.stl, ratButtonLargeBaseSharpTip.fcstd]
2015-10-23 batch upload of old designs
    [RatPoopScoop.fcstd, envSensorSet.ModelB.stl, envSensorSetCasePi2.fcstd, envSensorSetModelPi2.stl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]
2015-10-25 change session length to 30 min
    [MoueBoxInsertPart1.fcstd, MouseBoxInsertPart2.fcstd, mouseBoxDividerPart1.stl, mouseBoxDividerPart2.stl]
2015-11-08 cleanup and update Readme
    [sampleData.csv]
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2016-01-08 added freecad files
    [motionSensorOperantChamber.fcstd, raspiboxv3.fcstd]
2016-01-26 Added OpenSCAD file for pump assembly to the repo
    [pump_assembly.scad]
2016-01-26 Added dependences of pump_assembly.scad
    [bearings.scad, fasteners.scad, steppers.scad]
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2016-01-27 added scad module for mounting syringe pump on the cage assembly
    [pump_assembly.scad]
2016-01-27 Finished preliminary design for mounting syringe pump to cage assembly (see module cage_mount() in pump_assembly.scad)
    [pump_assembly.scad]
2016-02-01 updated pump assembly
    [pump_assembly.scad]
2016-02-01 blah blah resizing bearings blah
    [bearings.scad, pump_assembly.scad]
2016-02-02 Updated motor size
    [pump_assembly.scad]
2016-02-02 Updated idler end to use rubber bands to secure syringe
    [pump_assembly.scad]
2016-02-02 new hooks woot
    [pump_assembly.scad]
2016-02-02 Extended post and fixed backing on end idler
    [pump_assembly.scad]
2016-02-03 Resized syringe clamp relief to fit nut and bearings
    [pump_assembly.scad]
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2016-02-05 Resized nut trap and bearing relief down in SCAD design
    [pump_assembly.scad]
2016-02-05 pump controller program bookkeeping or whatever
    [pump_assembly.scad]
2016-02-05 herp derp resizing motor holes because why not
    [pump_assembly.scad, steppers.scad]
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2016-02-17 Began adjusting screws and adding recess to stabilize syringe plunger
    [pump_assembly.scad]
2016-02-17 first implementation of syringe holder
    [pump_assembly.scad]
2016-02-17 revised syringe holder to be much larger because 3D printers are for ants
    [pump_assembly.scad]
2016-02-17 removed unneeded mounting holes on idler end of pump assembly
    [pump_assembly.scad]
2016-02-17 Enlarged recesses for holding clamp screw caps while keeping thread holes the same. Intended for easier access when securing clamps.
    [pump_assembly.scad]
2016-02-18 Added cuts to the clamps on the idler end to allow for nuts to be positioned
    [pump_assembly.scad]
2016-02-18 back to square one - made relief for clamp rods thinner in hopes of them being held by pressure
    [pump_assembly.scad]
2016-02-18 reorganized files under openbehavior/pump-control into directories
    [bearings.scad, fasteners.scad, pump_assembly.scad, steppers.scad]
2016-02-19 newest iteration of carriage with syringe slot
    [pump_assembly.scad]
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2016-02-24 converted from freecad, working on the spout holder
    [alcoholSelfAdminFrame.scad]
2016-02-24 spout holder unit ready for test print
    [alcoholSelfAdminFrame.scad]
2016-02-24 adjusted the location of the spout, added a back wall but left an observation hole
    [alcoholSelfAdminFrame.scad]
2016-02-24 carving holes out of the frame for the spout holders
    [alcoholSelfAdminFrame.scad]
2016-02-25 added attachment screw to the spout holder, simplied the cylinders
    [alcoholSelfAdminFrame.scad]
2016-02-25 adjusted spout holder mounting position. added mounting hole in the frame
    [alcoholSelfAdminFrame.scad]
2016-02-25 adjusted the arrangement for the PCBs on the top
    [alcoholSelfAdminFrame.scad]
2016-02-26 rearranged the display if loop to move not used items to the bottom; disabled the screw holes on the side; getting ready for making the bottom plate
    [pump_assembly.scad]
2016-02-26 testing an assembly idea
    [pump_assembly.scad]
2016-02-26 minor adjustment of the top, ready for print
    [alcoholSelfAdminFrame.scad]
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2016-02-26 added a base for the pump
    [pump_assembly.scad]
2016-02-29 adjusted the sizes of the mounting grooves after a print
    [pump_assembly.scad]
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2016-02-29 updated end parts with solid base
    [pump_assembly.scad]
2016-03-01 modified the base board for the pump
    [pump_assembly.scad]
2016-03-01 can a small pin fool the printer
    [pump_assembly.scad]
2016-03-02 the pin fooled the rendering but not the printer head
    [pump_assembly.scad]
2016-03-02 making holes and curves to cut down printing time
    [pump_assembly.scad]
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2016-03-04 adjust step motor fastener length
    [alcoholSelfAdminFrame.scad]
2016-03-04 added top cover
    [alcoholSelfAdminFrame.scad]
2016-03-05 fixed dev board mounting holes to stop longlius fram offending the gods.
    [alcoholSelfAdminFrame.scad]
2016-03-07 adjusting the positions of the cutouts
    [alcoholSelfAdminFrame.scad]
2016-03-07 move the pi backwards to allow space for the dev-board. lowered pumpcontrl box height
    [alcoholSelfAdminFrame.scad]
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2016-03-08 reduce the hole size for the wires that go into the motor
    [pump_assembly.scad]
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2016-04-17 stand alone rfid reader case
    [rfidReaderCase.scad]
2016-04-18 shrink the size slightly, moved the mounting poles to touch the base.
    [rfidReaderCase.scad]
2016-04-19 adjusted size and locations based on the first print
    [rfidReaderCase.scad]
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2016-04-21 resize, add front cover
    [rfidReaderCase.scad]
2016-04-22 hole for potentiometer
    [rfidReaderCase.scad]
2016-04-26 Adjust the location of the Brightness potentiometer
    [rfidReaderCase.scad]
2016-04-26 modify front cover size
    [rfidReaderCase.scad]
2016-04-28 openscad version of the case
    [motionSensorCaseOperantChamber.scad]
2016-04-28 resize and other adjustments
    [motionSensorCaseOperantChamber.scad]
2016-04-29 rotate the Pi Box 90 degrees
    [motionSensorCaseOperantChamber.scad]
2016-05-01 re-orient the box so that it is not blocked by the spout holder
    [motionSensorCaseOperantChamber.scad]
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2016-05-25 adjust size
    [motionSensorCaseOperantChamber.scad]
2016-05-25 modify the position of the sensors and components
    [alcoholSelfAdminFrame.scad]
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2016-06-07 add RatSpoutHolderPlate for Med-Assocites operant chambers
    [ratSpoutHolderPlate.scad]
2016-06-10 adjust size of voltage converter holder
    [motionSensorCaseOperantChamber.scad, motionSensorOperantChamber.fcstd, raspiboxv3.fcstd]
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2016-06-29 holes for switch buttons
    [alcoholSelfAdminFrame.scad]
2016-06-30 increase plus maze height
    [plusmazeboots.scad]
2016-06-30 carve out spaces to reduce printing time
    [plusmazeboots.scad]
2016-06-30 RFID antennae housing
    [alcoholSelfAdminFrame.scad]
2016-07-02 top cover slant
    [alcoholSelfAdminFrame.scad]
2016-07-03 adjust the size of the top groove to fit the slant cover better
    [alcoholSelfAdminFrame.scad]
2016-07-04 adjust sizes for the top
    [alcoholSelfAdminFrame.scad]
2016-07-07 adjust hole locations
    [alcoholSelfAdminFrame.scad]
2016-07-07 add cue light to the spout holder
    [alcoholSelfAdminFrame.scad]
2016-07-08 the cue light now has an angle
    [alcoholSelfAdminFrame.scad]
2016-07-08 lower the rfid antenna case
    [alcoholSelfAdminFrame.scad]
2016-07-10 fastner for led cue light
    [alcoholSelfAdminFrame.scad]
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2016-07-11 enlarge the space for the bottom screws
    [pump_assembly.scad]
2016-07-11 moved mounting screws, +voltage converter
    [alcoholSelfAdminFrame.scad]
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2016-07-13 first draft
    [extinctionCase.scad]
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2016-07-14 case and cover
    [extinctionCase.scad]
2016-07-14 minor adjustment of lcd position
    [extinctionCase.scad]
2016-07-14 add powercord to the pi
    [extinctionCase.scad]
2016-07-15 Extinction box wiring documentation
    [ExtinctionBoxWiring.ods]
2016-07-15 add LED box designed by Cindy
    [extinctionCase.scad, extinctionLEDBox.scad]
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2016-07-15 adjust mounting columns
    [extinctionLEDBox.scad]
2016-07-19 add slots for viewing the LED on the Pi
    [extinctionCase.scad]
2016-07-20 adjust size of the LCD
    [extinctionCase.scad]
2016-07-20 add slant to spout holder
    [alcoholSelfAdminFrame.scad]
2016-07-24 add openning for LCD panel
    [alcoholSelfAdminFrame.scad]
2016-07-24 rfid antenna holder
    [alcoholSelfAdminFrame.scad]
2016-07-24 a bar to close the RFID antenna
    [alcoholSelfAdminFrame.scad]
2016-07-25 adjust RFID hook size
    [alcoholSelfAdminFrame.scad]
2016-07-25 minor adj position of the Pi
    [alcoholSelfAdminFrame.scad]
2016-07-25 minor adjust of mounting position
    [alcoholSelfAdminFrame.scad]
2016-07-28 enlarged the hook for RFID antenna
    [alcoholSelfAdminFrame.scad]
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2016-08-08 redesign brain slicer
    [brainMatrix.scad]
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2016-08-17 fix rubber band hooks sticking out
    [pump_assembly.scad]
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2016-11-15 further loosen syringe carrier to reduce friction
    [pump_assembly.scad]
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2018-10-09 shorter for better fit
    [rfid_antenna_loop.scad]
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

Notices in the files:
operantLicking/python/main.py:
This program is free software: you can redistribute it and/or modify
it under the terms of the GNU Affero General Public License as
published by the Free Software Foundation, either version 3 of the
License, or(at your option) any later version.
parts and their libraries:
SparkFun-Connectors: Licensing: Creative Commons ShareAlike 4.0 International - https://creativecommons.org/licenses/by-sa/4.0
